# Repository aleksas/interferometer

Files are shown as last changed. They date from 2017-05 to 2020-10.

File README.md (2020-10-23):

# Current version does not work due to critical errors in schematics

# Self mixing interferometer
Schematic designs and theoretical simulation to aid in building a self mixing optical interferometer.
Theoretical explanation of pcb purpose and circuit part choices explained in [this document](./documents/Laser_diode_modulation.pdf) (skip simulation details). 

General idea is explained in [the video](https://youtu.be/MUdro-6u2Zg?t=1291). More in depth eplanation can be found at least in [this publication](https://scihub.bban.top/10.1364/AOP.7.000570).

Main motivation is to develope a convinient device toplay around with self mixing interferometry. It provides significant improvement in precision over [ToF distance estimation](https://en.wikipedia.org/wiki/Time-of-flight_camera) ([Arduino ToF sensor](https://osoyoo.com/2019/04/21/arduino-lesson-vl53l0x-time-of-flight-distance-sensor/)). Apart from using in objct distance and speed estimation it also can be usefull for harmonic motion measurements, e.g. submicron vibrations.  

## Plan
- [ ] Update [current arduino shield](./pcb/) to make convinient self-mxing laser interferometry easily accesible
  - [ ] __Laser diode current modulation__
    - [ ] (Optional) Reproduce convinient SPICE simulation from [document (p. 34)](./documents/Laser_diode_modulation.pdf)
    - [x] Prepare board for convinient pcb manufacturing
      Capacitors, resistors, leds are loosely defined. Missing voltage and maybe other parameters. Entries like ARDUINO_SHIELD or measuring points only add to the confusion.  
      - [EasyEda](https://easyeda.com/aleksas_/self-mixing-laser-interferometer) | [LCSC](https://lcsc.com/)
    - [x] Optional: update [KiCAD model](./pcb/)
      - so that it visualizes electronic components in 3D
      - doesn't depend on deprecated symbols
    - [x] Assess the modulation frequency of ADN8810
      - [~333 kHZ](https://electronics.stackexchange.com/a/497173/249362)
    - [ ] Assess the probable performace of the board
      - [ ] Controlled by [Arduino DUE](https://www.arduino.cc/en/Guide/ArduinoDue) (preferred)
        - [ ] What is maximum laser diode modulation frequencynoredirect=1#comment1266315_497173)
        - [ ] What is the maximum precision of modulated current 
      - [ ] Controlled by [STM32F4DISCOVERY](https://www.st.com/en/evaluation-tools/stm32f4discovery.html)
        - [ ] What is maximum laser diode modulation frequency
        - [ ] What is the maximum precision of modulated current     
  - [ ] __Physical printed and assemled board validation__
    - [x] Assemble board and connect to Arduino or arduino form factor development board
    - [x] Write [software to control PCB laser diode modulation](./arduino/Uno_R3/modulation/modulation.ino)
      - [Code for modulatin ADN8810 from arduino](https://github.com/analogdevicesinc/arduino/blob/486ce99954853b3e9f34e81e827f400b49ca4765/Arduino%20Uno%20R3/examples/CN0395_example/ADN8810.cpp#L117-L140)
      - [Arduino SPI Barometric Pressure Sensor](https://www.arduino.cc/en/Tutorial/BarometricPressureSensor)      
      - [Some code](./arduino)
    - [ ] Verify laser diode modulation input
    - [ ] Verify laser monitor diode signal has interference pattern
  - [ ] __Estimating values form monitor diode signal__
    - Arduino ADC (current solution implemented on PCB) or FPGA
- [ ] Software for theoretical signal simulation and distance,velocity estimation
  - [ ] [Python scripts for simulating and estimatimating values](https://gist.github.com/aleksas/e764e93894b7945427d594147ea23370)
    - [x] Distance to stationary object
    - [x] Distance and velocity of moving/stationary object
    - [ ] Velocity of moving object having noisy signal

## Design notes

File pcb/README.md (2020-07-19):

The implementation chosen is self mixing interferometry as the diode lasers were readily available therefore provided a good starting point to the approach chosen 
of self mixing interferometry. Includes design of a CW diode LASER driver, 
a transimpedance amplifier on the Photodiode section of the TO-18 laser diode with a -3dB cutoff of 200 kHz, 
an output high pass filter and the relevant control circuitry that allows the whole system to be tested and controlled with industry standard 32 bit, 
arduino form factor development boards such as the FREEDOM© series from NXP or the DISCOVERY© and NUCLEO© series from STMicroelectronics among others.

3D PCB view
[Interactive 3D preview](https://aleksas.github.io/interferometer)

## PCB Components

### [ADN8810 (ADN8810ACPZ)](https://www.analog.com/en/products/adn8810.html?doc=ADN8810.pdf) - 12-Bit High Output Current Source [by Analog Devices](https://www.analog.com/)
- [Data Sheet](datasheets/ADN8810.pdf) ([source](https://www.analog.com/media/en/technical-documentation/data-sheets/ADN8810.pdf))
- [Vendors](https://octopart.com/adn8810acpz-analog+devices-433821?r=sp)

### [OPA320 (OPA320SAIDBVT)](https://www.ti.com/product/OPA320) - Precision, 20-MHz, 0.9-pA, Low-Noise, RRIO, CMOS Operational Amplifier With Shutdown by [Textas Instruments](https://www.ti.com/)
- [Data Sheet](datasheets/opa320.pdf) ([source](https://www.ti.com/lit/ds/symlink/opa320.pdf?ts=1592210569432))
- [PSpice](spice/OPA320.LIB) ([source](https://www.ti.com/lit/zip/sbom437))
- [Vendors](https://octopart.com/search?q=OPA320SAIDBVT&currency=USD&specs=0)

### [ADR292 (ADR292GRUZ)](http://www.analog.com/ADR292) - Low Noise Micropower 4.096 V Precision Voltage Reference [by Analog Devices](https://www.analog.com/)
- [Data Sheet](datasheets/ADR291_292.pdf) ([source](https://www.analog.com/media/en/technical-documentation/data-sheets/ADR291_292.pdf))
- [Vendors](https://octopart.com/search?q=ADR292GRUZ&currency=USD&specs=0)

### Laser
#### ADL-65055TL - N-Type ALGalnP Visible Laser Diode by [Laser Comonents](https://www.lasercomponents.com/)/[Arima Lasers](https://www.arimalasers.com/)
- [Data Sheet](datasheets/adl-65055tl.pdf) (sources: [1](https://www.lasercomponents.com/fileadmin/user_upload/home/Datasheets/arima/655nm/adl-65055tl.pdf), [2](http://www.farnell.com/datasheets/43655.pdf?_ga=2.22848763.1942577091.1592211693-817925239.1592211693), [3](http://www.farnell.com/datasheets/43655.pdf))
- [PSpice](spice/ADL65055TL.lib) ([source](https://www.eit.lth.se/sprapport.php?uid=824))
- [Vendors](https://octopart.com/2008361-laser+components-23943555?r=sp)

#### LTLD505T - Laser Diode 650nm 2.6VDC AlGaInP Laser Diode by [Lite-On Electronics](https://www.liteon.com/)
- [Data Sheet](datasheets/LTLD505T.pdf) ([source](https://www.jameco.com/Jameco/Products/ProdDS/2120428.pdf))
- [Vendors](https://octopart.com/ltld505t-lite-on-18796936?r=sp)

### [FDC637BNZ](https://www.onsemi.com/products/discretes-drivers/mosfets/fdc637bnz) - N-Channel 2.5V Specified PowerTrench MOSFET by [ON Semiconductor](https://www.onsemi.com)
- [Data Sheet](datasheets/FDC637BNZ-D.pdf) ([source](https://www.onsemi.com/pub/Collateral/FDC637BNZ-D.pdf))
- [PSpice](spice/FDC637BNZ.lib) ([source](https://www.onsemi.com/pub/Collateral/FDC637BNZ.lib))
- [Vendors](https://octopart.com/fdc637bnz-on+semiconductor-84325753?r=sp)

## References
- [Original project by Kiogora](https://github.com/Kiogora/interferometer)
  - [Whitepaper](https://github.com/aleksas/interferometer/raw/master/documents/Laser_diode_modulation.pdf)

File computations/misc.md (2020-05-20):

# Maximum current change frequency for [ADN8810](https://www.analog.com/media/en/technical-documentation/data-sheets/ADN8810.pdf) controlled by [Arduino Due](https://store.arduino.cc/arduino-due).

The maximum SCLK frequency, according to the [datasheet](https://www.analog.com/media/en/technical-documentation/data-sheets/ADN8810.pdf), is 12.5 MHz, and 
a transfer takes 16 bits, so that limits update rate to (12.5 / 16) MHz = 100 MHz / 128 = 781 kHz.

Settling time of the output of 3 µs, so, for accurate output after every write will take 16 / 12.5 µs + 3µs, 
but that's just latency; effective possible rate of accurate change is 1/(3µs) = 333.33 kHz.

From fig. 13 one can see that the output impedance, however, starts drastically changing after ca. 1 kHz, 
so whether or not that works for you: depends on what you attach to it.

## Arduino Due
A 84 MHz ARM Cortex-M3 like used on that board should do a couple MHz of SPI rate, easily. 
Depending on efficient the Arduino SPI library – it might or might not be simple and close to the metal – 
but software is easy to replace; [FreeRTOS](https://www.freertos.org/) runs on the [Arduino Due](https://store.arduino.cc/arduino-due), 
so it may save form maneuvering into a development dead-end if the Arduino software platform doesn't work.

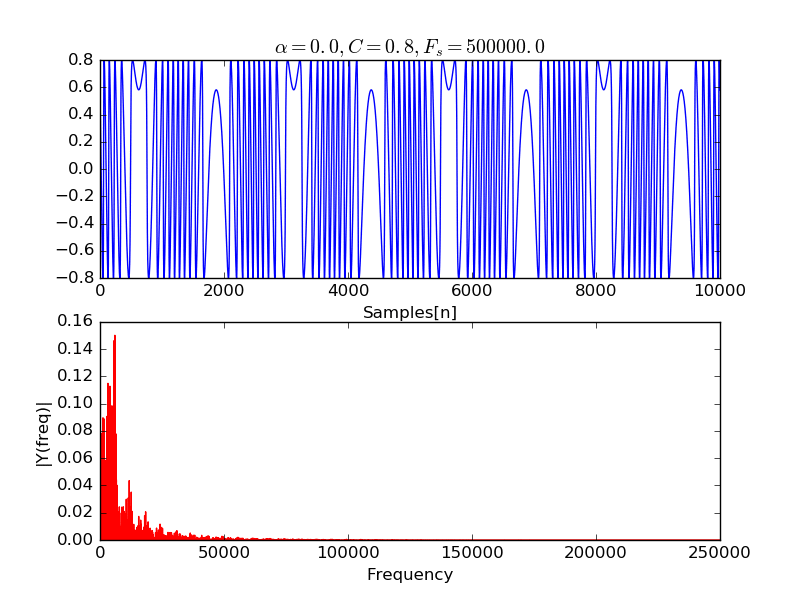
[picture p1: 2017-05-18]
computations/gifs/linewidth.gif

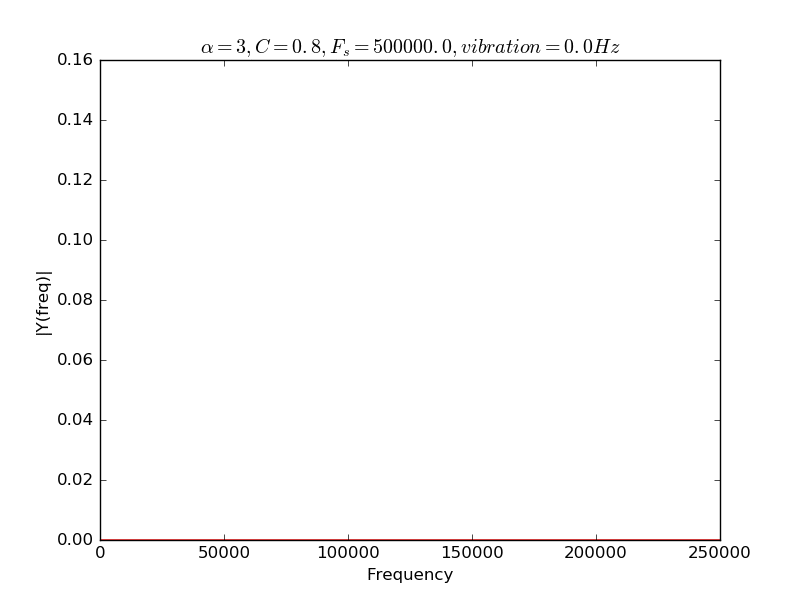
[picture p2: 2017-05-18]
computations/gifs/vibration.gif

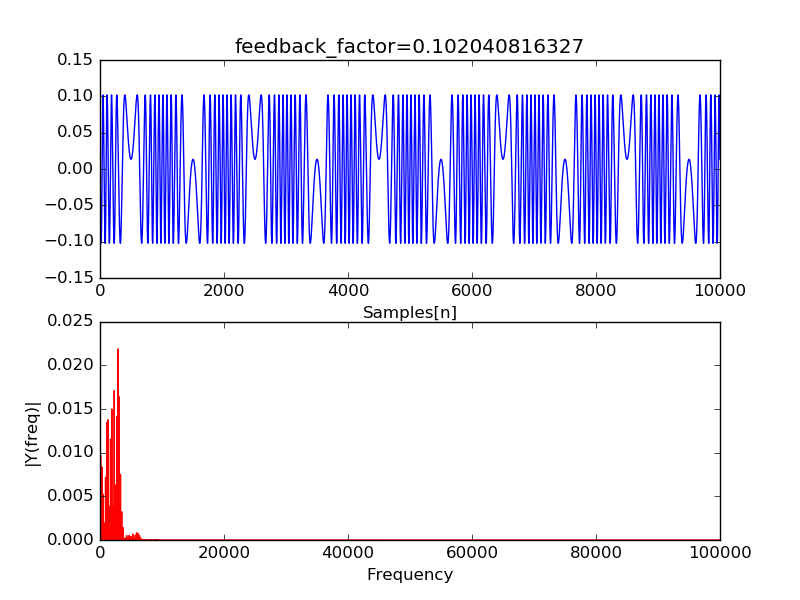
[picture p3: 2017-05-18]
computations/gifs/feedback_slow.gif

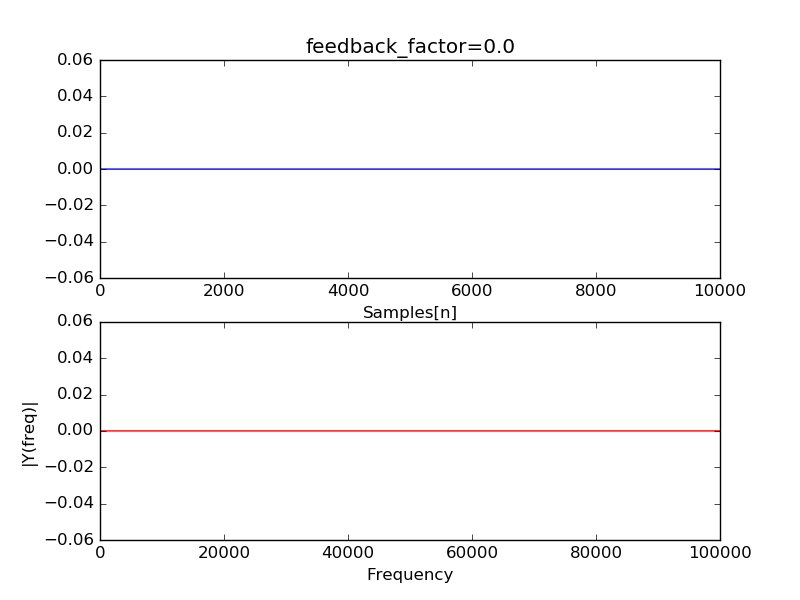
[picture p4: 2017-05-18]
computations/gifs/feedback_fast.gif

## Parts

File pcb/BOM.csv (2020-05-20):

References | Qty | Description | Manufacturer | MPN | Manufacturer | MPN | Manufacturer | MPN | Digikey | Mouser | RS | Newark | Farnell | LCSC
C1, C2, C3, C4, C5, C6, C7, C11, C13, C14, | 10 | 0.1uF 0603 Capacitors_SMD:C_0603_1608Metric | Yageo | CC0603KRX7R8BB104 | AVX | 06035C104K4T2A | KEMET | C0603C104K3RACTU | 399-7845-1-ND | 603CC603KRX7R8BB104 | 8015340 | 68R4780 | 2478241 | C56476
C8, C9, C10, | 3 | 22uF 0603 Capacitors_SMD C_0603_1608Metric | TDK | C1608X5R1A226M080AC | Murata | GRM188C80J226ME15D | Yageo | CC0603MRX5R5BB226 | 311-1815-6-ND | 810C1608X5R1A226M | 9159114 | 82AC9295 | 2494232 | C84419
C12, | 1 | 82pF 0603 Capacitors_SMD:C_0603_1608Metric | AVX | 04025A820FAT2A | KEMET | C0603C820F5GACTU | Murata | GRM0335C1H820GA01D | 399-7959-6-ND | 81GRM1555C1H820JA1D | 1356754 | 96Y7085 | 1740575 | C193091
R1, | 1 | 680KOhms 0805 1% Resistors_SMD:R_0805_2012Metric | Panasonic | ERA6AEB684V | Yageo | RC0805FR-07680KL |  |  | P680KDACT-ND | 667ERA6AEB684V | 1848863 | 62W9121 | 9237976 | C137499
R2, | 1 | 21KOhms 0805 1% Resistors_SMD:R_0805_2012Metric | Panasonic | ERA6AEB2102V | Yageo | RC0805FR-0721KL |  |  | P21KDADKR-ND | 603RC0805FR0721KL | 7086519 |  | 1652956 | C137569
R3, | 1 | 66.5Ohms 0805 0.1% Resistors_SMD:R_0805_2012Metric | TE Connectivity | RQ73C2A66R5BTDF | Panasonic | ERA6AEB66R5V |  |  | A140755DKR-ND | 667ERA6AEB66R5V | 1233070 |  | 3229398
R4, | 1 | 7.87KOhms 0805 Resistors_SMD:R_0805_2012Metric | Panasonic | ERA6AEB7871V | TE Connectivity | RN73C2A7K87BTG |  |  | P7.87KDACT-ND | 667ERA6AEB7871V | 7088690P |  | 1809824 | C413747
R5, R6, R7, R8, | 4 | 100KOhms 0805 Resistors_SMD:R_0805_2012Metric | TE Connectivity | CPF0805B100KE | Panasonic | ERA-6AEB104V | TE Connectivity | RN73C2A100KBTDF | P100KDACT-ND | 667ERA6AEB104V | 566765 | 08N2143 | 1577686 | C96346
R9, | 1 | 220Ohms 0805 Resistors_SMD:R_0805_2012Metric | TE Connectivity | CPF0805B220RE1 | Panasonic | ERA6AEB221V | Vishay | CRCW0805220RFKEAHP | P220DADKR-ND | 71CRCW0805220RFKEAH | 566913 | 01X1371 | 1577649 | C114519
R10, | 1 | 100Ohms 0805 Resistors_SMD:R_0805_2012Metric | Panasonic | ERA6AEB101V | TE Connectivity | 2-2176091-4 | TE Connectivity | CPF0805B100RE1 | P100DACT-ND | 667ERA6AEB101V | 7217662 |  | 1750741 | C143843
R11, | 1 | 5.1KOhms 0805 Resistors_SMD:R_0805_2012Metric | Panasonic | ERA6AEB512V | Vishay | CRCW08055K10FKEA |  |  | P5.1KDACT-ND | 667ERA6AEB512V | 6791569P |  | 1670237 | C186492
D1, D2, | 2 | LED GREEN LEDs:LED_0805_2012Metric_Castellated | Lite-On | LTST-C171KGKT | Lite-On | LTST-C190GKT | Avago | HSMG-C190 | 160-1183-1-ND | 859LTSTC190GKT | 6920975 | 68Y1165 | 2497374 | C98224
LD1, | 1 | Laserdiode_N_TYPE ADN8810ACPZ:ADL-65055TL | LASER COMPONENTS | ADL-65055TL |  |  |  |  |  |  |  |  | 1272658
Q1, | 1 | 50V Vds, 0.22 A Id, N-channel MOSFET, SOT-23:SOT95P280X145-6N | ON Semiconductor | FDC637BNZ |  |  |  |  | FDC637BNZCT-ND | 512FDC637BNZ |  | 95W3155 | 2322581 | C68302
U1, | 1 | ADN8810ACPZ ADN8810ACPZ:ADN8810ACPZ | Analog Devices | ADN8810ACPZ |  |  |  |  | ADN8810ACPZ-ND | 584ADN8810ACPZ | 7089833 | 27X8183 | 2377083
U2, | 1 | Dual CMOS Operational Amplifiers, Zero-Drift Series, 1.8-V, microPower:SOT95P280X145-6N | Texas Instruments | OPA320SAIDBVT |  |  |  |  | 296-36434-1-ND | 595OPA320SAIDBVT |  | 33AH4590 | 3004957
U3, | 1 | ADR292GRUZ ADN8810ACPZ:ADR292GRUZ | Analog Devices | ADR292GRUZ |  |  |  |  | ADR292GRUZ-ND | 584ADR292GRUZ | 7098168 | 14AC3018 | 2727741

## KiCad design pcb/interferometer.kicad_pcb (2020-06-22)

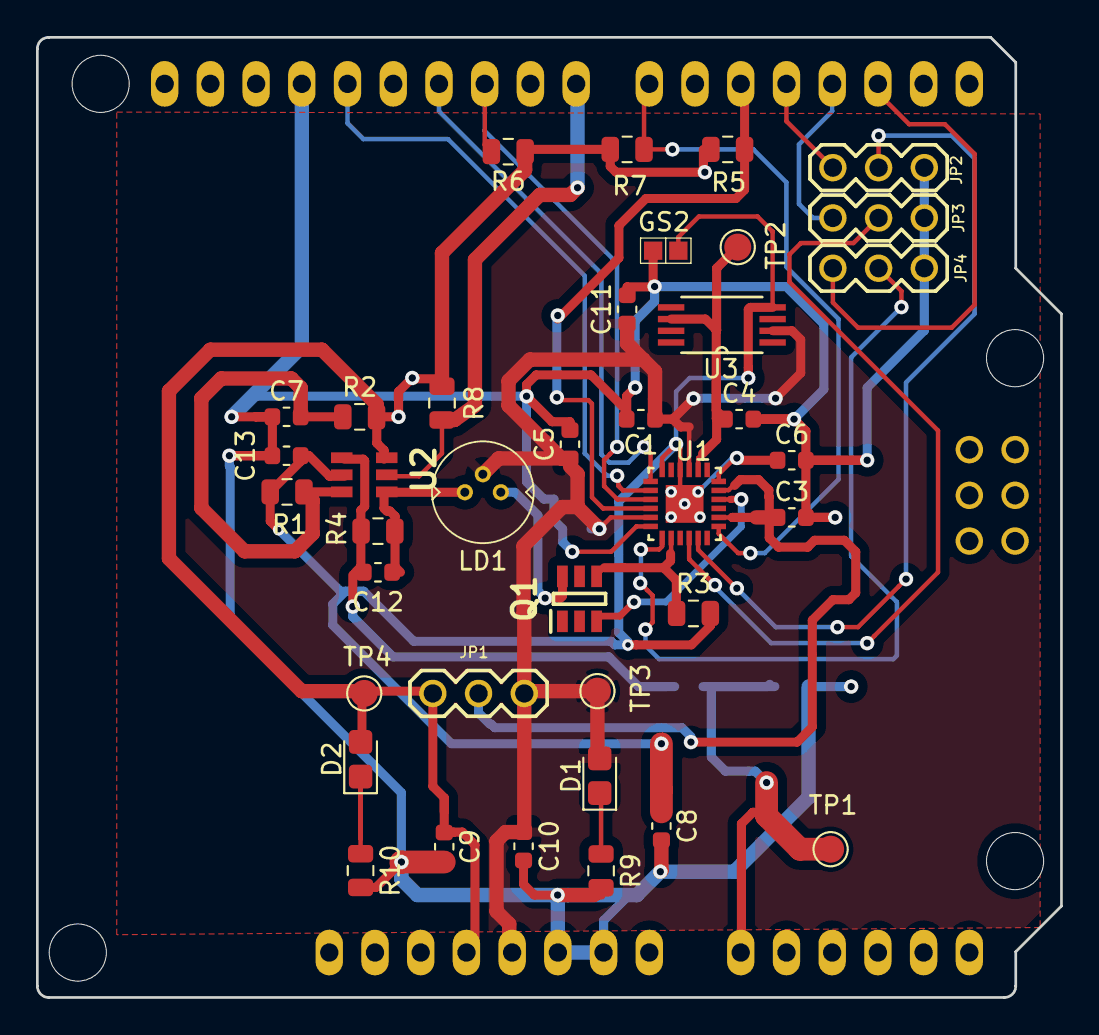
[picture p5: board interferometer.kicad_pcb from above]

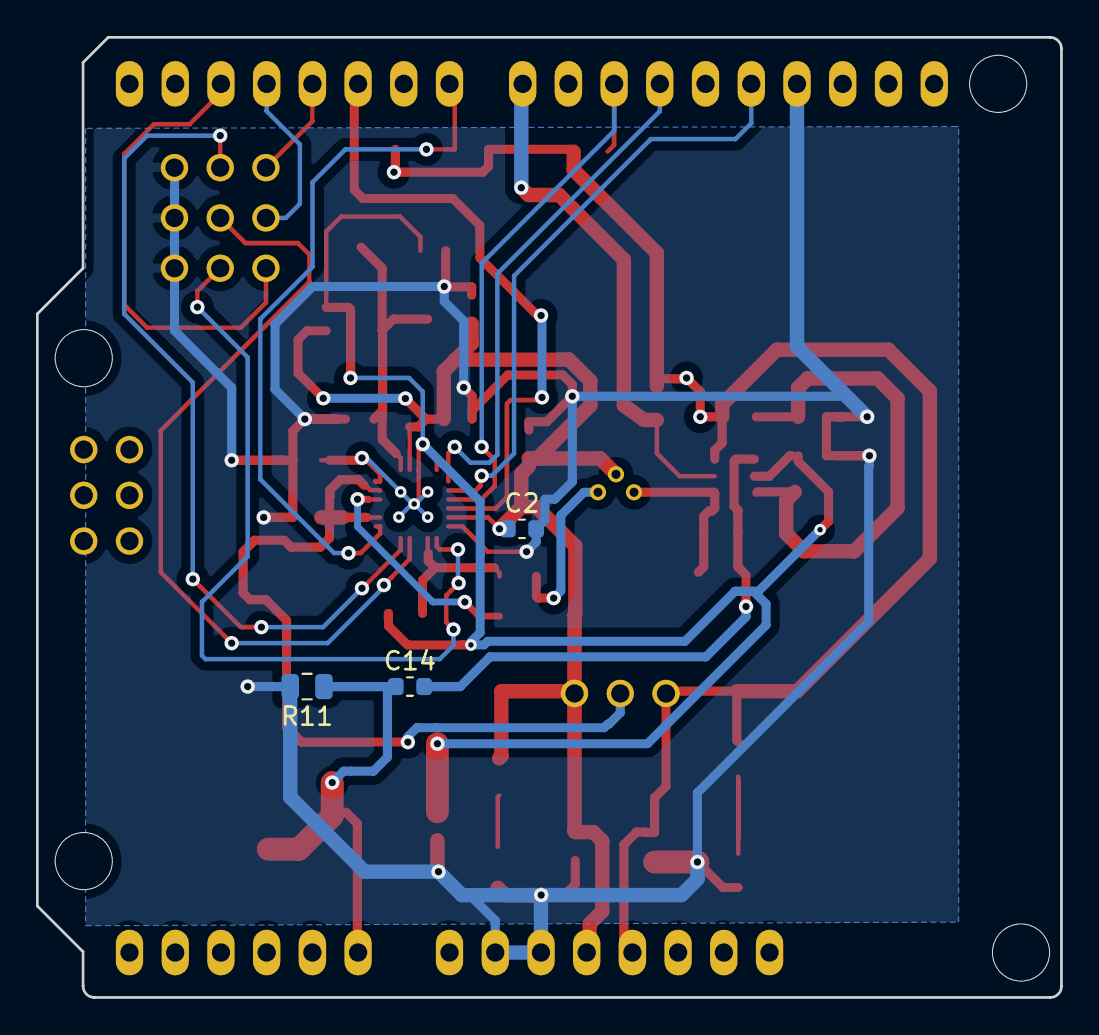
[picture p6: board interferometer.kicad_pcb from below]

Board: 2 copper layers, 56.9 x 53.3 mm, 42 parts (3 on the bottom side), 27 nets.

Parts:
C1, C2, C3, C4, C5, C6, C7, C11, C13, C14: 0.1uF; C_0603_1608Metric
C8, C9, C10: 22uF; C_0603_1608Metric
C12: 82pF; C_0603_1608Metric
D1, D2: LED; LED_0805_2012Metric_Castellated
J1: GS2
JP1, JP2, JP3, JP4: Jumper_NC_Dual; 1X03
LD1: Laserdiode_N_TYPE; ADL-65055TL
Q1: FDC637BNZ; SOT95P280X145-6N
R1: 680k; R_0805_2012Metric
R2: 21k; R_0805_2012Metric
R3: 66.5R; R_0805_2012Metric
R4: 7.87k; R_0805_2012Metric
R5, R6, R7, R8: 100k; R_0805_2012Metric
R9: 220R; R_0805_2012Metric
R10: 100R; R_0805_2012Metric
R11: 5.1k; R_0805_2012Metric
SHIELD1: ARDUINO_SHIELD
TP1, TP2, TP3, TP4: TESTPOINT; TestPoint_Pad_D1.5mm
U1: ADN8810ACPZ
U2: OPA320SAIDBVT; SOT95P280X145-6N
U3: ADR292GRUZ

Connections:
/3v3: C9.1, D2.2, JP1.3, R2.1, R5.1, R6.1, R7.1, R8.1, SHIELD1.3V3, TP4.1, U2.6
/4.096_VREF: C4.1, TP2.1, U1.14, U3.6
/5v: C1.1, C2.1, C5.1, C10.1, C11.1, D1.2, JP1.1, LD1.2, SHIELD1.5V, TP3.1, U1.15, U1.23, U3.2
/A0: C14.1, R11.1, SHIELD1.AD0, TP1.1
/ADDR0: JP2.3, SHIELD1.4
/ADDR1: JP3.3, SHIELD1.3
/ADDR2: JP4.3, SHIELD1.2
/AVSS: C6.1, C8.1, C13.1, J1.1, R1.1, R3.2, U1.12, U1.16, U1.18, U1.25, U2.2, U3.4
/IOUT: Q1.3, U1.10
/LD: LD1.1, Q1.6
/MOSI: SHIELD1.11, U1.19
/PD: C12.2, LD1.3, R4.2, U2.4
/RSN: Q1.4, R3.1, U1.2
/SCK: SHIELD1.13, U1.20
/chip_addr0: JP2.2, U1.5
/chip_addr1: JP3.2, U1.4
/chip_addr2: JP4.2, U1.1
/~CS: R6.2, SHIELD1.10, U1.21
/~SHDN: R8.2, SHIELD1.8, U2.5
/~laser_reset: R5.2, SHIELD1.5, U1.22
/~laser_standby: R7.2, SHIELD1.7, U1.7
Earth: C1.2, C2.2, C3.2, C4.2, C5.2, C6.2, C7.1, C8.2, C9.2, C10.2, C11.2, C13.2, J1.2, JP2.1, JP3.1, JP4.1, R9.2, R10.2, R11.2, SHIELD1.GND1, SHIELD1.GND2, SHIELD1.GND3, U1.24
unnamed: C3.1, JP1.2, U1.8, U1.11
unnamed: C7.2, R1.2, R2.2, U2.3
unnamed: C12.1, C14.2, R4.1, U2.1
unnamed: D1.1, R9.1
unnamed: D2.1, R10.1

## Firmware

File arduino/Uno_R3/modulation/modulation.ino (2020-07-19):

#include <SPI.h>
#include <Arduino.h>

#define CSADN8810_PIN            10
#define IO5ADN8810_PIN           5
#define IO7ADN8810_PIN           7

#define SERIAL_COMM           false

#define ADN8810_ADR                 0x00   // Hard wired device address
#define ADN8810_RSN                 66.2f  // Ohms

#define ADN8810_FULL_SCALE_OUT      4095
#define ADN8810_HALF_SCALE_OUT      2048
#define ADN8810_QUARTER_SCALE_OUT   1024

#define ADN8810_CHOSEN_MAX_VALUE 1024
#define ADN8810_CHOSEN_MIN_VALUE 512

#define ADN8810_VALUE_COUNT (ADN8810_CHOSEN_MAX_VALUE - ADN8810_CHOSEN_MIN_VALUE)
#define ADN8810_VALUE_HALF_COUNT (ADN8810_VALUE_COUNT / 2)

#define ADN8810_DELAY_US 50

typedef enum {
  ADN8810_DISABLE,
  ADN8810_ENABLE
} enADN8810Status;

void ADN8810_MasterPower(enADN8810Status status)
{
  if (status == ADN8810_ENABLE)
    digitalWrite(IO7ADN8810_PIN, HIGH); // enable master power on IO5
  else if (status == ADN8810_DISABLE)
    digitalWrite(IO7ADN8810_PIN, LOW);
}

void ADN8810_Reset(void)
{
  /* Reset DAC: Make RESET IO7 logic 0 */
  digitalWrite(IO5ADN8810_PIN, LOW);
  delay(1); // delay 1ms
  digitalWrite(IO5ADN8810_PIN, HIGH);
}

void ADN8810_Init(void) {
  pinMode(IO5ADN8810_PIN, OUTPUT); /* Set IO5ADN8810 pin as output */
  pinMode(IO7ADN8810_PIN, OUTPUT); /* Set IO7ADN8810 pin as output */

  ADN8810_MasterPower(ADN8810_ENABLE); //  enable master power on IO5

  ADN8810_Reset(); // Reset DAC
}

void SPI_Write(uint8_t ui8address, uint8_t ui8data)
{
  /* Set ADN8810 CS low */
  digitalWrite(CSADN8810_PIN, LOW);

  /* Send first byte */
  SPI.transfer(ui8address);
  /* Send second data byte */
  SPI.transfer(ui8data); // 8 data bits

  /* Set ADN8810 CS high */
  digitalWrite(CSADN8810_PIN, HIGH);
}

void setup() {
  if (SERIAL_COMM) { 
    Serial.begin(9600);
  
    while (!Serial) {
      ; // wait for serial port to connect. Needed for native USB port only
    }
  }
  
  /* Initialize SPI */
  SPI.begin();
  SPI.setDataMode(SPI_MODE0);
  
  ADN8810_Init();
}

inline void witeCode(uint16_t code){
    uint8_t ui8UpperByte = 0;       /* Data byte MSB */
    uint8_t ui8LowerByte = 0;       /* Data byte LSB */

    /* build 12 bits of data + 4 bits of device address */
    ui8UpperByte = (uint8_t)(((code & 0xF00) >> 8) | (ADN8810_ADR << 4)); // 4 address and 4 data bits
    ui8LowerByte = (uint8_t)(code & 0xFF); // 8 bits of data
    
    SPI_Write(ui8UpperByte, ui8LowerByte);
}


uint16_t i = 0;
float code = ADN8810_CHOSEN_MIN_VALUE;
float delta = (ADN8810_CHOSEN_MAX_VALUE - ADN8810_CHOSEN_MIN_VALUE) / (1.0f * ADN8810_VALUE_HALF_COUNT);

void loop() {
  witeCode((int16_t) code);
  code += delta * ((i < ADN8810_VALUE_HALF_COUNT) ? 1 : -1);
  
  i = (i + 1) % ADN8810_VALUE_COUNT;
  
  delayMicroseconds(ADN8810_DELAY_US);
  
  if (SERIAL_COMM) {   
    Serial.print(code);
    Serial.print(' ');
    Serial.print(delta);
    Serial.print('\n');
  }
}

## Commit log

2017-05-18 Modify schematic
    [interferometer.sch]
2017-05-21 Modify design
    [interferometer.sch, interferometer.xlsx]
2017-05-21 finalise layout
    [interferometer.kicad_pcb, interferometer.sch]
2017-05-21 Output gerbers
    [interferometer.kicad_pcb]
2017-05-21 Output gerbers(protel file extensions)
    [interferometer-B.Cu.gbl, interferometer-B.Mask.gbs, interferometer-B.SilkS.gbo, interferometer-Edge.Cuts.gm1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]
2017-05-21 design postprocessing
    [interferometer.kicad_pcb]
2017-05-22 modify design for manufacturing
    [interferometer-B.Cu.gbl, interferometer-B.Mask.gbs, interferometer-B.SilkS.gbo, interferometer-Edge.Cuts.gm1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]
2020-05-20 Update project. Cleanup.
    [1-click-bom.csv, 6pin IC.stp, 8pin IC.stp, CP_24_1_ADI-L.step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]
2020-05-28 add arduino code
2020-06-15 Kitspace path update.
    [BOM.csv]
2020-06-19 Add liteon laser diode datasheet
